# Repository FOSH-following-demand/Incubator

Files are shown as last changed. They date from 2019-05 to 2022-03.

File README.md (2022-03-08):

# Incubator

MboaLab in Cameroon were awarded a $750 grant by the Build Free and Open Science Hardware Project led by Andre Chagas and supported by the Mozilla Foundation to build a low-cost, open-source incubator for microbiology.

**Why an incubator?**
Most biology labs in Cameroon and elsewhere in resource-constrained contexts are under-equipped due to the high cost of lab equipment and it is essential for many protocols including open enzyme manufacturing to have optimal growth temperature for important microrganisms such as _Escherichia coli_ bacteria. 

**Why open hardware?**
We believe that DIY and Open Science Hardware can facilitate access to low-cost and high-quality equipment for biology labs in Cameroon, Ghana and beyond. 

All resources are openly licensed and linked below. Future plans include the inclusion of orbital shaking which increases aeration of cultures and therefore the yield of micro-organisms and their products like proteins.

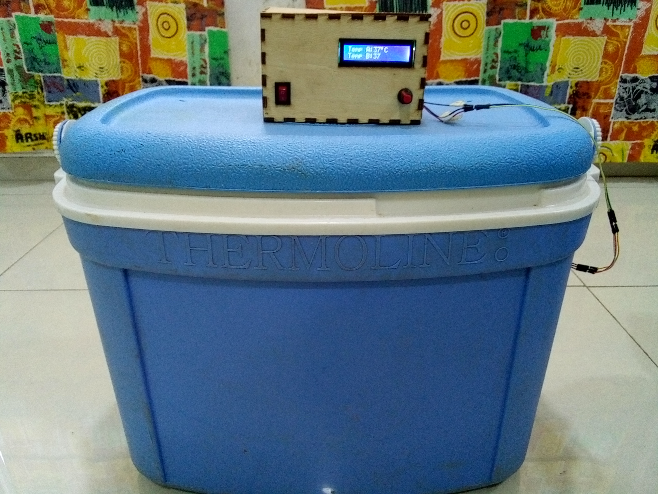
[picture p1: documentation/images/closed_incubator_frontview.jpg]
closed incubator frontview


# Build you own incubator

 - If you would like to build the device, get started by following the [build documentation](https://github.com/FOSH-following-demand/Incubator/tree/master/documentation/building)
 - The folders in this repository contain details of the [materials needed](https://github.com/FOSH-following-demand/Incubator/tree/master/hardware/BOM), laser cut design for the [enclosure](https://github.com/FOSH-following-demand/Incubator/tree/master/hardware/enclosure), the Arduino-based [electronics design](https://github.com/FOSH-following-demand/Incubator/tree/master/hardware/electronics) and firmware.
 - If you have questions or suggestions for improvements, please [add an issue](https://github.com/FOSH-following-demand/Incubator/issues) or make a pull request.

# Related Links

-   Documentation of Hive BioLab build on [Benchling](https://benchling.com/harry_akligoh/f/lib_UTO5lXRH-hive-biolab/etr_TNTAtGl7-building-and-testing-a-37-deg-celsius-incubator/edit)
-   Documentation of Hive BioLab build on [WikiFactory](https://wikifactory.com/+biolabkh/incubator)

# Acknowledgements

-   Ongola FabLab and OER Cameroon Team: Ariel Kameni and Yves Obame
-   Kumasi Hive Makerspace Team: Evans Tetteh-Djangbah and Isaac Atia-Abugbilla 
-   Image credits for Incubator: MboaLab Team

# Licensing

Software released under [MIT License](https://opensource.org/licenses/MIT) //
Hardware released under [CERN Open Hardware License v1.2](https://ohwr.org/cern_ohl_s_v2.txt)

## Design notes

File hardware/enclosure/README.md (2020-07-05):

### Summary

This folder contains 2D CAD files designed to be laser cut in 4 mm plywood or acrylic to form the electronics casing to be mounted on top of the cooler box.
Both PDF and dxf files are provided to suit different laser cutter requirements.

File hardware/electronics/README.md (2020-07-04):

## Electronics Diagram

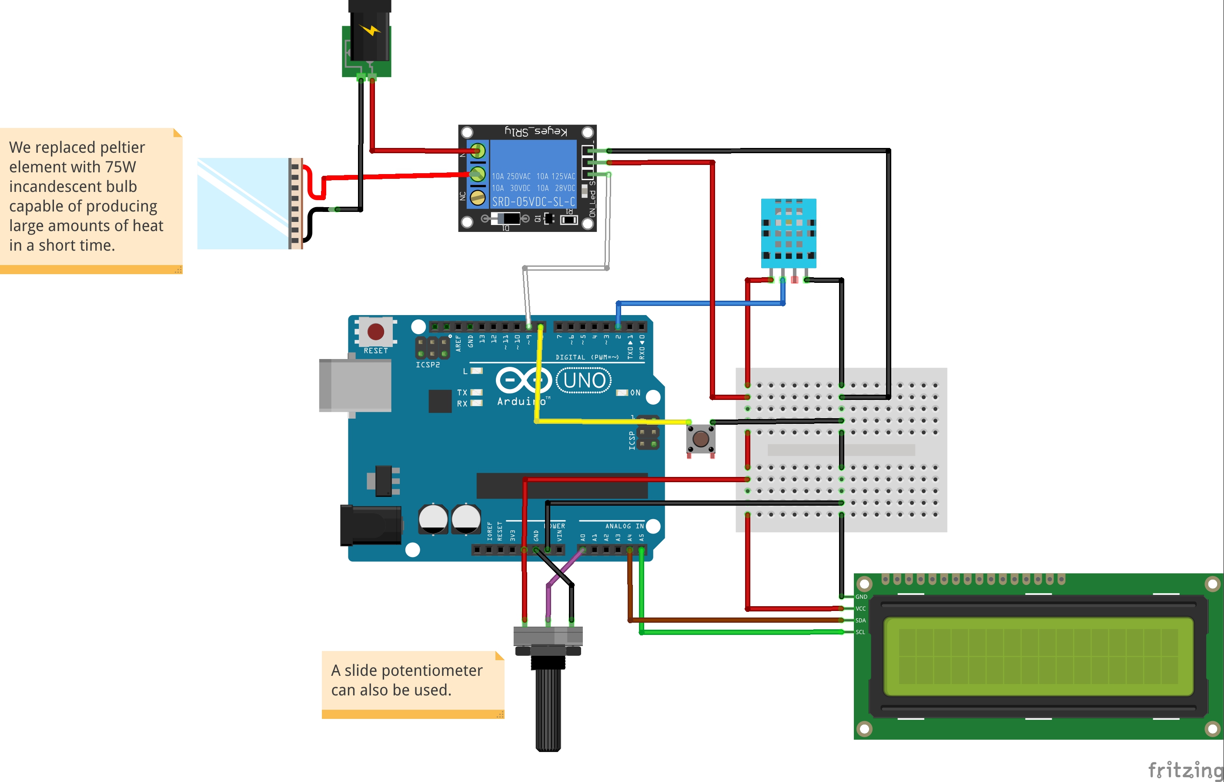
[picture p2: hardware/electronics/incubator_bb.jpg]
Arduino diagram


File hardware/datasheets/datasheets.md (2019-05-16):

#### Add to this folder all the datasheets used in the build.

This will make it easier for people to learn what each part is doing in case they need to substitute parts.

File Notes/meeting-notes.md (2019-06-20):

## June 20, 2019

Note taker: Julieta

- Incubator is working well, will test with yoghurt making tomorrow.
- Will complete info on local suppliers this week, with the link Andre provided
- Will upload arduino code and the laser cut patterns to the repo

The team wants to try making the shaker, as it's very easy and they have the materials, will take one or two days.

In terms of usability and democratization, next step is producing a "KossamTor" - An incubator for Kossam (yoghurt), that will be installed in the village for people to produce yoghurt. Presentation will be 3rd july, during MboaLab opendoors day. For this, the team will make a video and short instructions, for people that don't use GitHub (most of them).

Will try to buy stuff asap so to send Andre the invoices before 24th.

## June 14, 2019

Note taker: Julieta

1- Updates on development of the prototype     
- Assembled 1st version of incubator and it works!
- You can actually choose temperature :D

2- Document for the user
- BoM ready with $ (check hw folder BoM)
- Send information for contributing to map of suppliers --> Possible output of BFOSH: map with suppliers

3- Next
- Let's complete the docs: hw/datasheets, software: the code, readme file: steps to build it, steps to use it, any lesson learned, specifics people need to know to replicate the incubator??
- Test incubator by making yoghurt!

Next call: June 20th

## June 6, 2019

Note taker: Julieta

1- Updates on development of the prototype     
- Tested how long the chamber can keep hot water -- document this test! Maybe a journal can help, so documentation is not done at the end of the project (it's a pain and we tend to document only success)
- Started coding with Arduino IDE based on Biohack Academy's code combined with Richard Boman's incubator (biomakers challenge)
- Still working on the code, will upload 1st version soon

2- Program schedule, week 3: BoM, dev plan     
- Materials: goal is to get everything locally. Got sensors in mboa lab, but trying to source them locally (in progress). 
- Get BoM & simple dev plan, will 

3- Difficulties      
- Still learning github - Julieta will record & send video tutorial 

Next call: June 13th

## May 30, 2019

Notetaker: Andre

Status:
 - Made document showing different materials other projects used.
 - Decided for the cooler box, since this is already built and has been optimized for holding temperature.
 - They also saw a shop that repairs fridges, maybe using an out of order fridge, might be an option (to be tested later maybe)
 - Found temperature sensor kits and Arduino at Mboalab. 

Questions:

 - how to test the incubator to know that it is working? and how can people building it will know that their built is working? (testing and calibration).
 - Would it be possible to log the data? Register the temperature being read by the arduino in a file, so that the data can be plotted later.

before next meeting:
 
 - Write down a BOM and Document! https://github.com/FOSH-following-demand/Incubator/blob/master/hardware/BOM/BOM.md

Next meeting:

- Agenda:  
 
 -- check how the building of the first prototype is going, see if there are any problems.   
 -- If things are already working properly, think about testing/calibrating and writing a manual for other people to build.  
 
## May 23, 2019

Status quo on the project:

Questions: What material to use for the frame - wood, metal, which metal - should be low-cost and durable.
Options: impregnated wood or insulated with styrophome

Local suppliers in Yaoundé - add to this list: https://github.com/FOSH-following-demand/local_suppliers/blob/master/electronic_components.csv

Next local meeting Friday, May 24
- Agenda items:

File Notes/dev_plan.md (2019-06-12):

# Development plan

Use this file to store your plan for the program. What are you going to do, in which order? 

| Week        | Activities           | Who           |
| ----------- | -------------------- | ------------- |
| 1           |Research existing work related to incubator                |  Thomas and Yves             |
| 2           |What material to use for the frame                      |Lenshina and Yves              |
| 3           |Find Local suppliers and buy equipment                       |Lenshina, Thomas, Ariel, Marius|
| 4           |Build the electronic Part                     | Lenshina, Thomas, Yves, Marius, Ariel              |
| 5           |Assemble the Version 1 of the Incubator. Start the Shaker                      |Lenshina, Thomas, Yves, Marius, Ariel |

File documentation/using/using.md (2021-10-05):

## DIY Incubator Operation Manual

### Installation and Setup 

The DIY incubator is top-opened. The latter should be placed on a low-level surface to facilitate handling and use.

1. Make sure that the incubator is off and plug-in the power cable on normal sector current (220V-240V);
 
2. Switch on the device using the power button located at the level of the control box. (The incandescent bulb within the incubator should light up and information about the temperature inside the cooler box should be displayed on the LCD screen);

3. Place desired items inside the cooler box; (While placing items in the cooler box, care must be taken to avoid direct contact with the incandescent bulb).
 
4. Close the lid of the cooler box;
 
5. Use the potentiometer (rotary button) of the electronic control box to input the desired temperature. 
*(The light bulb will stay on until the desired temperature is obtained inside the cooler box; Once the desired temperature is obtained, the incandescent bulb will then start to continuously come on and off to regulate and maintain the temperature stable inside the cooler box).*
 
6. To stop the incubator, switch off the power button. 
*(No program option to time the incubation is currently available, Use an external timer during operation).*

### Handling routine:
The DIY incubator should be thoroughly disinfected and cleaned before and after each incubation.

### Features:
The device has an auto-resume function (in case of power outage, the incubation will automatically continue as soon as current is back with set conditions maintained without any external internvention needed);

### Troubleshooting:
a.  The LCD screen is on but the incandescent bulb doesn’t turn on:
1.  replace the bulb;
2.  replace the bulb holder;
3.  replace the I2C relay module

Links:
https://openbioeconomy.org/projects/open-source-microbiology-incubator/
https://github.com/FOSH-following-demand/Incubator/tree/master/software

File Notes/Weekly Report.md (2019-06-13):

Brief summary of the progress made, learnings, and way forward in keywords by week

#### Week1
We have made a list of similar DIY incubator projects. In addition to this, Andre sent us several links to other incubator projects.  

#### Week 2
We did a reseach on What material to use for the frame (wood, metal, which metal - should be low-cost and durable). Finally we come out with this comparative table and we decide to use the cooler box. 

| Type of Material used for Incubator Shell/Insulation material | Pros                                                                                                                      | Cons                                                                                                                                                          | Optimisation                     |
|---------------------------------------------------------------|---------------------------------------------------------------------------------------------------------------------------|---------------------------------------------------------------------------------------------------------------------------------------------------------------|----------------------------------|
| Acrylic                                                       | ·      Attractive visibly                                                                                                 | Expensive                                                                                                                                                     | N/A                              |
|                                                               | ·      Does not require any manual work/designing as all parts are sculpted and cut using the 3D printer and laser cutter |                                                                                                                                                               |                                  |
|                                                               |                                                                                                                           | 3D printer and laser cutter required to assemble parts                                                                                                        |                                  |
| Wood/plywood                                                  | ·      Cheap and available locally                                                                                        | Liable to rot due microorganisms and moisture                                                                                                                 | Impregnating                     |
|                                                               | ·      Light and can easily be incorporated in field models                                                               | Plywood breaks if not carefully handled                                                                                                                       |                                  |
|                                                               |                                                                                                                           |                                                                                                                                                               |                                  |
| Glass                                                         | ·      Attractive visibly                                                                                                 | Fragile to work with as  it breaks easily                                                                                                                     | N/A                              |
|                                                               |                                                                                                                           |                                                                                                                                                               |                                  |
| Stainless Steel sheet metal                                   | ·      Rust and corrosion- resistant                                                                                      | ·      Expensive                                                                                                                                              | N/A                              |
|                                                               | ·      Easy to clean                                                                                                      | ·      Prone to overheating                                                                                                                                   |                                  |
|                                                               |                                                                                                                           | ·      Heavy                                                                                                                                                  |                                  |
|                                                               |                                                                                                                           |                                                                                                                                                               |                                  |
| Polystyrene foam (Styrofoam) box                              | ·      Cheap and available locally                                                                                        | Favours bacterial and fungal growth                                                                                                                           | N/A                              |
|                                                               | ·      Light and can easily be incorporated in field models                                                               | Can be damaged in the process of cleaning/sterilisation                                                                                                       |                                  |
|                                                               | ·      Recommended to achieve lower ambient temperatures (< 25 °C),                                                       | Melts easily in case of over heating                                                                                                                          |                                  |
| Hard Plastic cooler box                                       | ·      Cheap and available locally                                                                                        |                                                                                                                                                               | N/A                              |
|                                                               | ·      Easy to clean and sterilize                                                                                        |                                                                                                                                                               |                                  |
|                                                               | ·      Can achieve a set temperature of 37 °C to 44.5 °C                                                                  |                                                                                                                                                               |                                  |
|                                                               | ·      Takes less time approximately 45 - 96 minutes to reach set temperature                                             |                                                                                                                                                               |                                  |
|                                                               | ·      Energy consumption stands at 0.78 - 1.05 kWh/24h in cold environments (3.5 to 7.5 °C)                              |                                                                                                                                                               |                                  |
| Cardboard box                                                 | ·      Cheap and readily available                                                                                        | ·      Not waterproof so easily gets destroyed by moisture                                                                                                    | Insulating with polystyrene foam |
|                                                               | ·      Light and can easily be incorporated in field models                                                               | ·      Not heat-resistant so gets burned in case of over heating                                                                                              |                                  |
|                                                               |                                                                                                                           | ·      Incubator shell has to be shut tight to avoid heat dissipation and this is very difficult to achieve with cardboard boxes without the survival blanket |                                  |
|                                                               |                                                                                                                           | ·      Not recommended for use at lower ambient temperatures since this set up with similar to slightly                                                       |                                  |
|                                                               |                                                                                                                           | ·      Greater power consumption observed                                                                                                                     |                                  |

#### Week 3
The team was so glad to found local suppliers selling all what we need here in Cameroon: DBL electronics and Megatec

| Name of the local suppliers  | Localisation on google map                | Contact                                                                                                                   |
|------------------------------|-------------------------------------------|---------------------------------------------------------------------------------------------------------------------------|
| DBL electronique             | https://maps.app.goo.gl/5ZiqXomu7RbgKoKo7 |  - Yaoundé (+237698282538/+237673687133) - Douala (+237699675349/+237678830266) - Bafoussam (+237668095091/+237605076456) |
| Megatec Electronic           | https://maps.app.goo.gl/c4DdAgbu1jX4qPhZ9 | +237677524208                                                                                                             |

#### Week4
This week was so productive, we focus our efforts on electronics: 
- First of all, we decided on what we want our incubator will be able to do. Specifically, we want to be able to fixe the desired temperature with a potentiometer and bring the incubator at this temperature.  
- We had an issue on the cooling system of the incubator. Fan VS Peltier elements. Finally we choose the Peltier element
- We bought the required electronics
- Ariel from Ongola Fablab, helps us with the Arduino code and all looks great

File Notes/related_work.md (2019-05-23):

# Related projects

| Project name  | URL           | Active/Not active | Notes - relevance |
| ------------- | ------------- | ----------------- | -------------- |
| Hackteria| https://hackteria.org/wiki/index.php/DIY_Incubator| Active | |
| Biodesign| https://biodesign.cc/2013/12/25/diy-incubator/ | Active |  |
| Instructables|https://www.instructables.com/id/Low-cost-and-accurate-incubator-for-DIY-biology/|Active|  |
|Biomaker|https://www.biomaker.org/projects/2018/1/29/open-source-lasercut-portable-incubator-for-microbiology|Active|

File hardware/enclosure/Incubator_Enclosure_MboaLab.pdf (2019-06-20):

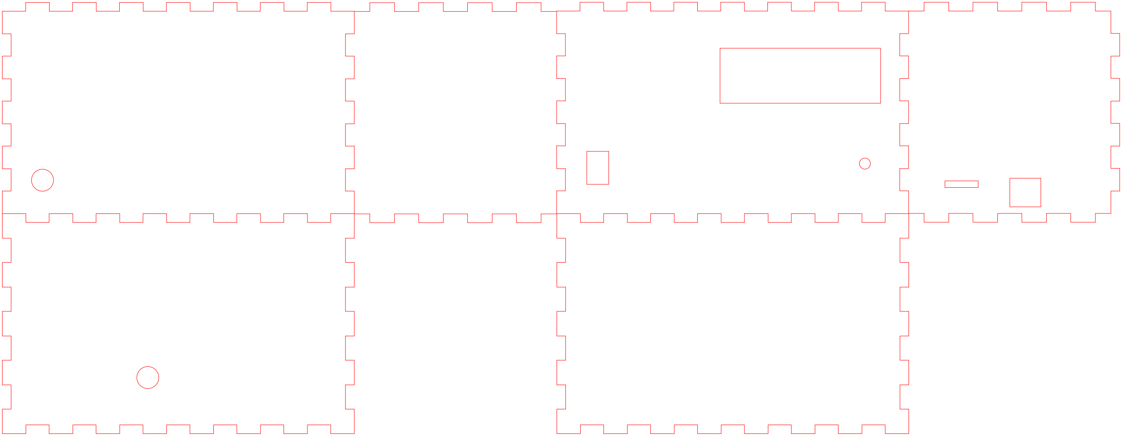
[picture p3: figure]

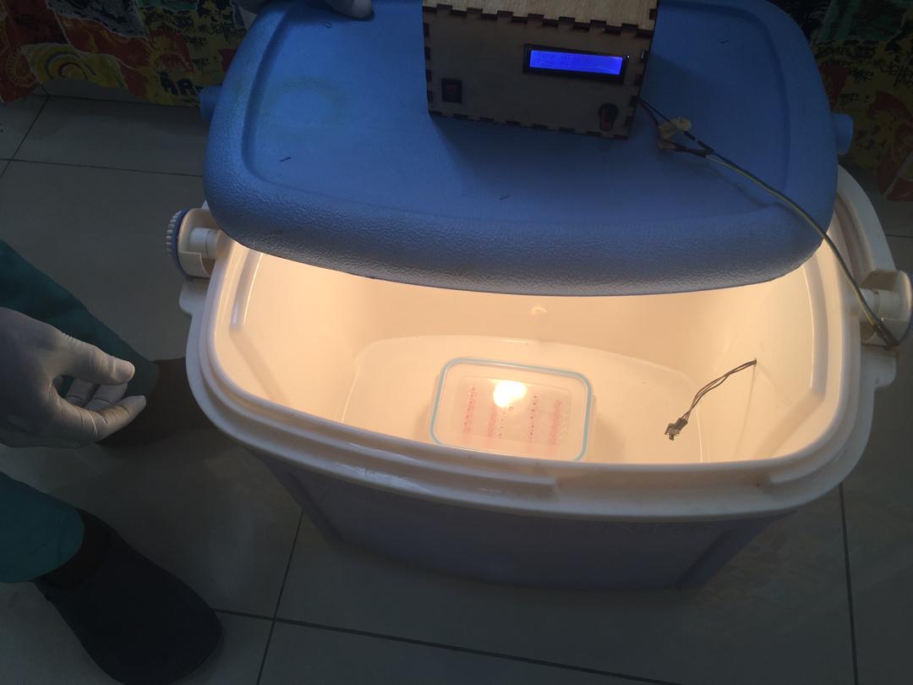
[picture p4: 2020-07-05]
documentation/images/open_incubator_topview.jpg

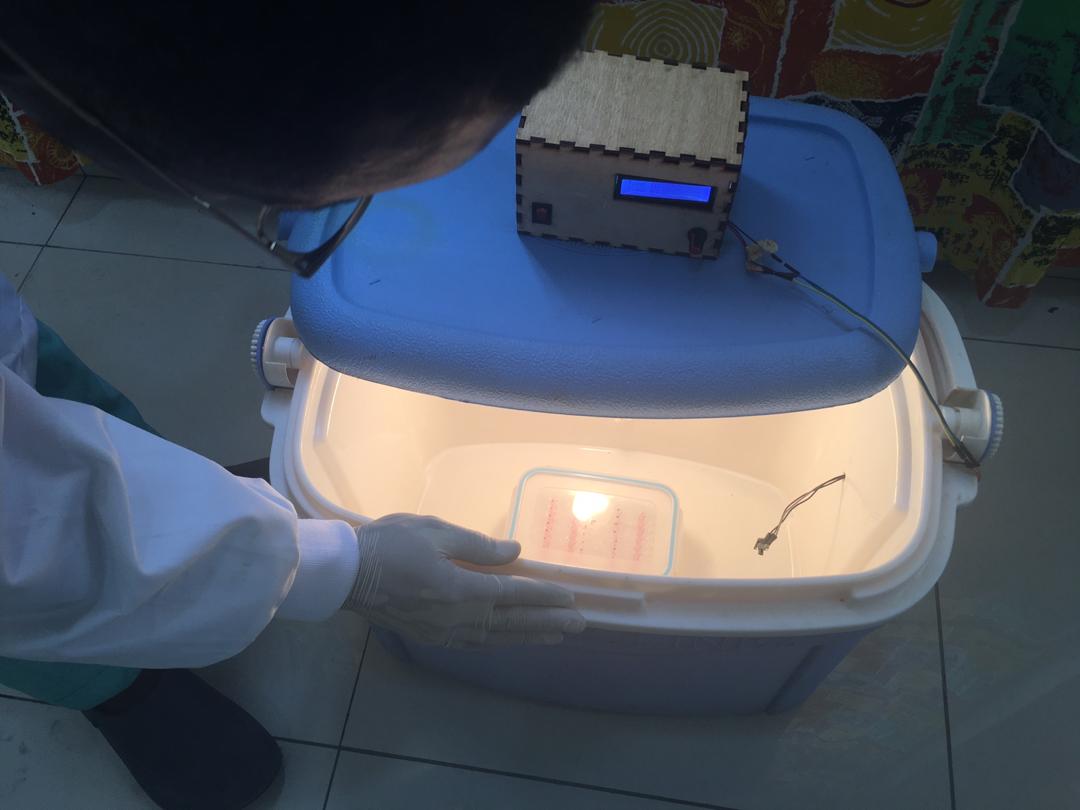
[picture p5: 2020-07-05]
documentation/images/open_incubator_topview2.jpg

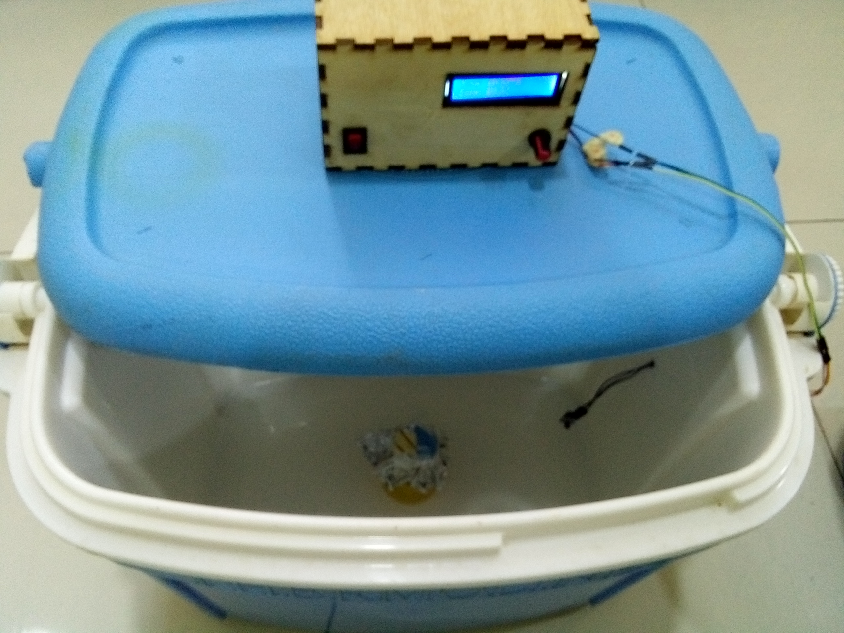
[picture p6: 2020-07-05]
documentation/images/closed_incubator_topview.jpg

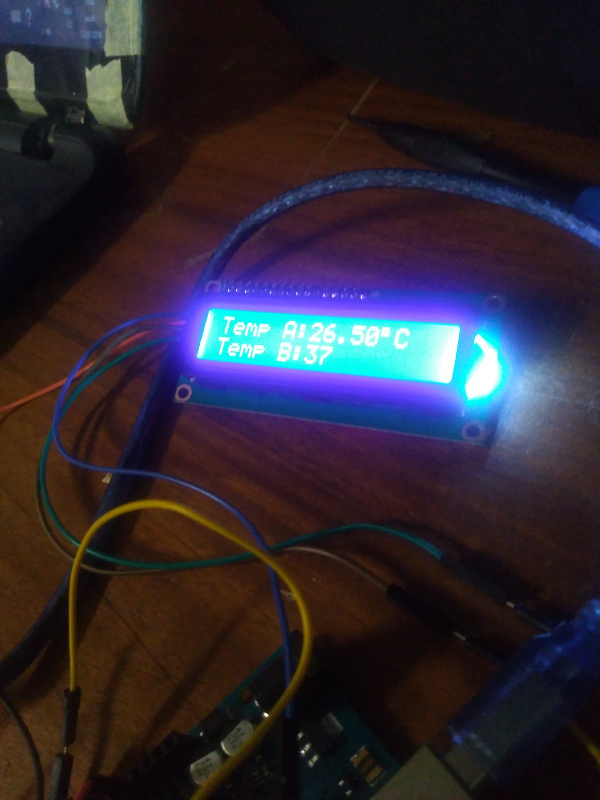
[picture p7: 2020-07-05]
documentation/images/lcd_display.jpg

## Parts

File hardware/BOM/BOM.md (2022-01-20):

## Electronics and Hardware
| N° | Quantity | Description                 | Local supplier   | Cost (F CFA) | Datasheet |
|----|--------|-----------------            |------------------|--------------|--------------|
| 1  | 1      | Arduino Uno (Version: Rev.3)                | [DBL Electronique]| 7000         | [Datasheet](https://github.com/FOSH-following-demand/Incubator/blob/master/hardware/datasheets/Arduino_Uno.pdf) |
| 2  | 1      | 1602 LCD Display Module (1602A-1)     | DBL Electronique | 3000         | [Datasheet](https://github.com/FOSH-following-demand/Incubator/blob/master/hardware/datasheets/1602A.pdf)|
| 3  | 1      | 1-Channel 5V  I2C Relay Module for Arduino | DBL Electronique | 1500         | [Datasheet](https://github.com/FOSH-following-demand/Incubator/blob/master/hardware/datasheets/Datasheet%20for%20ELC3003.pdf)          |
| 4  | 1      | Step Down Power Supply Module (Hi-Link HLK-PM01 AC-DC 100-240V to 5V DC/3W  | DBL Electronique | 3000         | [Datasheet](https://github.com/FOSH-following-demand/Incubator/blob/master/hardware/datasheets/HLK-PM01-Hi-Link_Step%20Down%20Power%20Supply%20Module.pdf)          |
| 5  | 1      | Temperature Sensor 18B20                  | DBL Electronique | 3500         | [Datasheet](https://github.com/FOSH-following-demand/Incubator/blob/master/hardware/datasheets/DS18B20.pdf)|
| 6  | 1      | USB 2.0 A to B Cable (Model Number:U022-010-R)             | DBL Electronique | 1000         | [Datasheet](https://github.com/FOSH-following-demand/Incubator/blob/master/hardware/datasheets/1951363_USB%20Cable.pdf)          |
| 7  | 10     | Jumper Wires (Male to Male) 40 x 6" (150mm) Adafruit PRODUCT ID: 758 | DBL Electronique | 2000          |  [Datasheet](https://github.com/FOSH-following-demand/Incubator/blob/master/hardware/datasheets/758_Web_Jumper%20wire.pdf)         |
| 8  | 10     | Dupont Wire (20CM, Color Jumper Cable, 2.54mm 1P-1P Male to Female)                | DBL Electronique | 2000          | [Datasheet](https://github.com/FOSH-following-demand/Incubator/blob/master/hardware/datasheets/40P-MF-Dupont-Wire.pdf)          |
| 9  | 1      | Rotary Potentiometer - 100k Ohm, Linear, Panel Mount*               | DBL Electronique | 250          | [Datasheet](https://github.com/FOSH-following-demand/Incubator/blob/master/hardware/datasheets/Rotary%20PDB18.pdf)          |
| 10 | 1      | Breadboard Solderless ABS, 7mm to 8mm (Part Number MCBB400)              | DBL Electronique | 1500         | [Datasheet](https://github.com/FOSH-following-demand/Incubator/blob/master/hardware/datasheets/Breadboard-roboromania.pdf)          |
| 11 | 1      | Standard IEC 1.5mm Electrical cable, PVC Flexible Cable 3 Core White in 1M Cut Length | DBL Electronique | 2500         | [Product Info](https://www.electricpoint.com/3093y-1-5mm-pvc-flexible-cable-three-core-white-1m.html)          |
| 12 | 1      | Incandescent bulb A60 Frosted Glass 75W 240V*          | Hardware store   |500           | [Product Info](https://shengfeng.en.made-in-china.com/product/myWnqOVUEehM/China-A60-Incandescent-Bulbs-Light-Frosted-Glass-75W-240V-Ce-RoHS.html)         |
| 13 | 1      | Light Bulb Holder, 10x E27 ES Edison Screw Cap Socket Light Bulb Holder Fitting Lamp Fixing Base          | Hardware store  |2000           | [Product Info](https://www.amazon.co.uk/Edison-Socket-Holder-Fitting-Fixing/dp/B01NBSVVJ2)           |
| 14 | 1      | Cooler box Thermoline® 50x30 cm*               | Local Markets    | 25 000       |     /      |
| 15 | 1      | 4 mm plywood or colored acrylic                 | Local Markets    |    /    |     /      |
| 16 | 1      | ON/Off Red LED Light illuminated Rocker Switch (RL-15-11/N-C-2-RE/BK-P1-S-2)  | DBL Electronique| 600  | [Datasheet](https://github.com/FOSH-following-demand/Incubator/blob/master/hardware/datasheets/Rocker-switches.pdf)           |
| 17 | 1      | Wood glue, Top bond® white adhesive wood glue,500g    | Hardware store| 2000  | [Product Info](https://m.made-in-china.com/product/Good-Price-Top-Bond-Furniture-White-Adhesive-Liquid-Wood-Glue-832258715.html)  |
| 17 | 1      | Acrylic glue, WELD-ON 4 Acrylic Adhesive - 4 Oz + Applicator Bottle with Needle | Hardware store| 10000  | [Product Info](https://www.amazon.com/Weld-Acrylic-Adhesive-Applicator-Bottle/dp/B0096TWKCW/?&tag=gluefaq-20#descriptionAndDetails)  |
| 18 | 1      | GOLDSCREW PZ DOUBLE-COUNTERSUNK MULTIPURPOSE SCREWS 5 X 50MM 200 PACK (16497) | Hardware store| 4000  | [Product Info](https://www.screwfix.com/p/goldscrew-pz-double-countersunk-multipurpose-screws-5-x-50mm-200-pack/16497#product_additional_details_container)  |

* The lightbulb could be replaced with another heater e.g. a PCB heater element or a Peltier element
* Rotary potentiometer could also be used
* Other cooler box dimension could be used (100W Incandescent bulb should be usef for bigger cooler boxes)

## Mechanical

- Laser Cutter 
- Electric drill

## Tools

- Soldering kit
- Universal Screwdriver
- Double-sided tape
- Digital multimeter
- Wire cutter

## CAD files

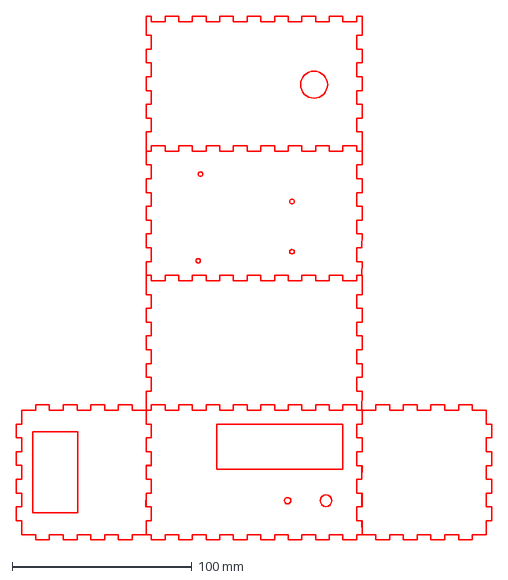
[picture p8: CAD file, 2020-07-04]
hardware/enclosure/Incubator_Enclosure_Hive.dxf
264.0 x 291.0 mm

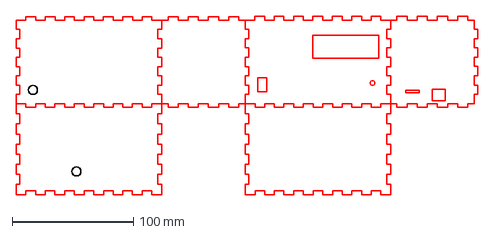
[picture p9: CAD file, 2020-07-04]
hardware/enclosure/Incubator_Enclosure_MboaLab.dxf
381.0 x 147.1 mm

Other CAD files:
hardware/enclosure/Incubator_Enclosure_Hive.dwg

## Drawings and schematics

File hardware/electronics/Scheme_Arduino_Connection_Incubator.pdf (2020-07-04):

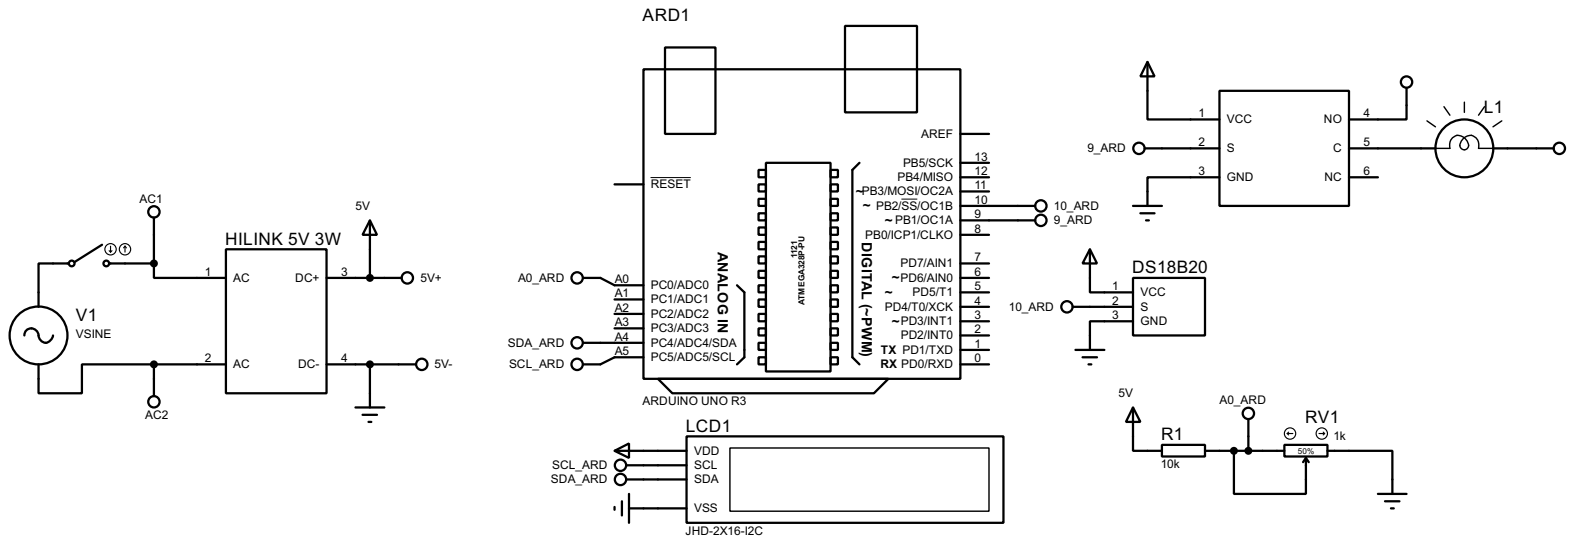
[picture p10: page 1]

DIGITAL (~PWM) ANALOG IN ATMEGA328P-PU 1121 ~~ ~~~~ TXRX PD0/RXD 0 PD1/TXD 1 PD2/INT0 2 PD3/INT1 3 PD4/T0/XCK 4 PD5/T1 5 PD6/AIN0 6 PD7/AIN1 7 PB0/ICP1/CLKO 8 PB1/OC1A 9 PB2/SS/OC1B 10 PB3/MOSI/OC2A 11 PB4/MISO 12 PB5/SCK 13 AREF PC5/ADC5/SCL A5 PC4/ADC4/SDA A4 PC3/ADC3 A3 PC2/ADC2 A2 PC1/ADC1 A1 PC0/ADC0 A0 RESET ARD1 ARDUINO UNO R3 R1 10k 50%RV11k VSS SCL VDD SDA LCD1 JHD-2X16-I2C L1 5V AC 1 AC 2 DC+ 3 DC- 4 HILINK 5V 3W V1 VSINE 5V AC1 AC2 5V+5V- SCL_ARD SDA_ARD SDA_ARD SCL_ARD VCC 1 S 2 GND 3 NO 4 C 5 NC 6 9_ARD 9_ARD 10_ARD A0_ARD VCC 1 S 2 GND 3 DS18B20 10_ARD A0_ARD

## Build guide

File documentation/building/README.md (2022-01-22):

## Getting started with assembly

This equipment is an incubator, designed to keep the contents at a constant temperature above the ambient temperature. It is an insulated box (a cooler box) that contains a heater (lightbulb), a temperature sensor and some electronics and software that will control the temperature to keep it constant at the level input by the user.

The primary use case is microbiology. It is essential for many protocols to have optimal growth temperature for important microrganisms such as _Escherichia coli_ bacteria. However, mst biology labs in Cameroon and elsewhere in resource-constrained contexts are under-equipped due to the high cost of lab equipment. Other use cases include a drying chamber and a yoghurt maker.

To build the device you will need to undertake some basic soldering and load software onto an Arduino Uno microcontroller but you do not need to have prior experience as there are many tutorials and guides online. This build could be completed by one person in less than a day with all materials and facilities available.

If you have questions you can contact [@LabMboa](https://twitter.com/labmboa?lang=en) on Twitter or via email mboalab@gmail.com

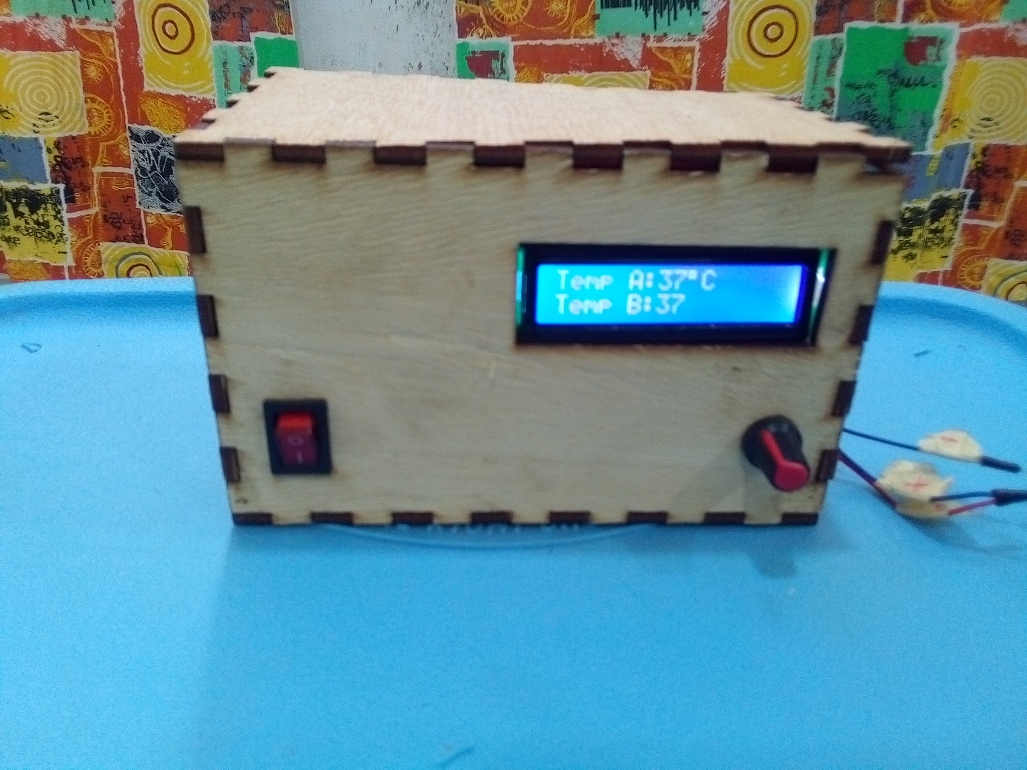
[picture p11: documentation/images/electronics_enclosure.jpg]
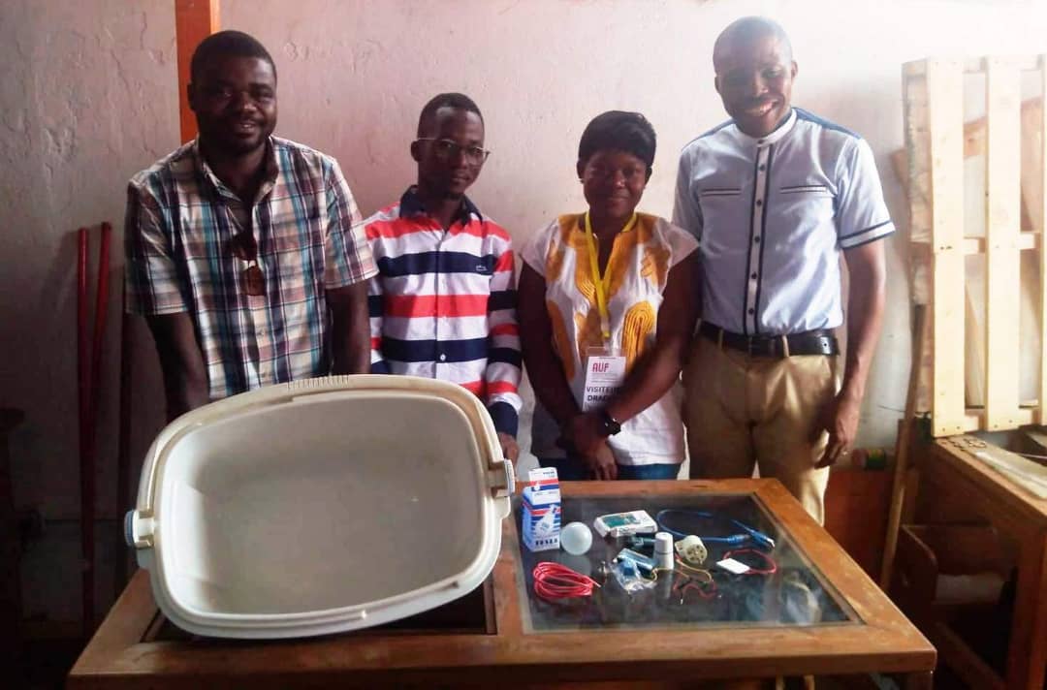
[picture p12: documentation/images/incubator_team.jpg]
   
<br>

## Gathering your materials

The list of components and tools required can be found in the [Bill of Materials](https://github.com/FOSH-following-demand/Incubator/blob/master/hardware/BOM/BOM.md). 

<br>

## Build Steps

### Assembling the electronics
1.	Gather all necessary equipment, electronics and sensors listed in the [BOM](https://github.com/FOSH-following-demand/Incubator/blob/88bb84b1b9b74473d8da1b99ba0d825d767e2a87/hardware/BOM/BOM.md), keep your soldering kit and Digital multimeter ready to check connections and normal operation after soldering. 
2.	Using jumpers and dupont wires, Carefully connect all the sensors and other modules to the Arduino Uno Rev.3 microprocessor and to the breadboard following the equipment’s [electronic circuit diagrams](https://github.com/FOSH-following-demand/Incubator/blob/88bb84b1b9b74473d8da1b99ba0d825d767e2a87/hardware/electronics/incubator_bb.jpg). Use a standard IEC 1.5mm Electrical cable to connect the relay module, light bulb and power supply module.
3.	Using a digital multimeter, check all connections and the normal flows of current in the whole electric circuit.

### Uploading the software to the arduino board
4.	Connect the Arduino UNO board to a computer with the latest version of [Arduino IDE](https://www.arduino.cc/en/software) installed using a USB 2.0 A to B Cable.
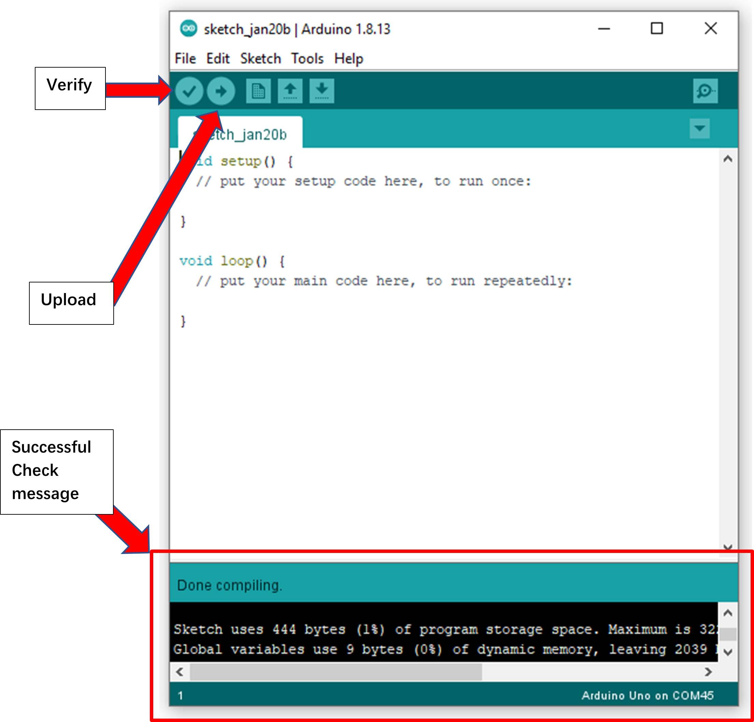
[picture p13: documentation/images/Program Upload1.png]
5.	Open the [Incubator.ino](https://github.com/FOSH-following-demand/Incubator/blob/88bb84b1b9b74473d8da1b99ba0d825d767e2a87/software/Incubator.ino) software and on the software interface, click on **verify** to make sure all necessary libraries are installed. Wait until the message **Done compiling** and specific information about the program appears as shown on the picture  .   
6.	Select the right port and on the software interface click on **upload** to upload the program to the board. Wait until the message **Done uploading** is displayed. 

### Constructing the electronics enclosure and Integrating the electronics
7.	Use the 2D CAD file: [Incubator_Enclosure](https://github.com/FOSH-following-demand/Incubator/blob/88bb84b1b9b74473d8da1b99ba0d825d767e2a87/hardware/enclosure/Incubator_Enclosure_MboaLab.pdf), to laser-cut plywood or acrylic to make the electronic enclosure of the incubator. 5mm colored acrylic or 4mm plywood is recommended. Use acrylic glue or Wood glue to assemble cut pieces and first mount the base of the box. 
8.	At this point, place the base above the cooler box cover at the location you want the electronic box to fit (center position preferred); 
9.	Use an electric drill to make a hole (1cm) crossing the acrylic and the entire depth of the cooler box cover.
10.	Drill another hole (1cm) on the side, just below the handle of the cooler box.
11.	Send the temperature sensor inside the cooler box through the created hole on the side. 
12.	Send light bulb cable through the created hole on the cooler box cover and carefully place all electronic parts inside the electronics enclosure.
13.	Use double side tape to fix the electronic enclosure to the cooler box cover.
14.	Screw the bulb holder on the donwnside of the cooler box cover and place an incandescent bulb. 
15.	Turn on the circuit and check if the light bulb is switched on and other sensors are operational.
16.	Place the cover of the electronic box (don’t use acrylic glue or Wood glue to seal the box) the cover should remain easily removable for maintenance.

### Checking that it works
17.	Use a separate thermometer to verify that the temperature reaches and is maintained at the correct set point.
18.	Check and follow [Using](https://github.com/FOSH-following-demand/Incubator/blob/e79139635490b86b92911df16381e2448330a7f6/documentation/using/using.md) for Operation Manual to ensure normal use and behavior of the equipment.

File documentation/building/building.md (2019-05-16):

**Use this folder to create files for building instructions:**
- Each equipment is going to have a different building process, but here are some suggestions on how to organise things:

<br>

1. getting started:
 - a brief overview of the equipment people are about to build and what kind of knowledge they are expected to have (soldering, programming). Also, is this safe for amateurs/kids? Is it a one person build? How much time does it take on average to build it?
 - Could you add contact information (email, forum, twitter handle) for people to reach out in case something goes wrong?

<br>

2. List of materials needed:
 - In the form of a table, containing part name, quantity and a couple of words on what they do. Extra points if the parts are divided according to the building steps (below)
 - Remember to include the tools necessary as well! (pliers, saw, computer, etc)  

 |part name| function  | quantity  | build step  | obs.  |
 |---|---|---|---|---|
 |LM2596| voltage regulator  | 2  | 3  | these could be substituted by XX  |
 | Nose needle Pliers  | hold components while soldering  | 1  | all steps  | regular pliers would also work  |

<br>

3. build steps:
 - Divide this section in as many subparts as you like and try to be as clear as possible. Would someone seeing the whole thing for the first time be able to build it? (it is a good exercise to oversee someone building the equipment using only your written/video/figure instructions)
 - Is a video a better way to instruct people how to use it? try to keep the file size as small as possible without compromising quality. Also reach out to us, as a good idea might be to create a different repository for the video files.  

<br>

4. Last checks before powering up/using for the first time:
 - Could people do one more check of everything before powering up things? Maybe double check that the capacitors were soldered in the proper orientation? Make sure there are no cut metal parts shorting the bottom side of the PCB? Make sure the area around the equipment is clear and won't be hit if the equipment has moving parts (eg shakers, centrifuges, etc).

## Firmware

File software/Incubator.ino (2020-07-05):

#include <Wire.h> 
#include <LiquidCrystal_I2C.h>
// #include <OneWire.h>
// #include <DallasTemperature.h>
// #define ONE_WIRE_BUS 2

// OneWire oneWire(ONE_WIRE_BUS);
// DallasTemperature sensors(&oneWire);
#include "DHT.h"

#define DHTPIN 2 
#define DHTTYPE DHT11
DHT dht(DHTPIN, DHTTYPE);
LiquidCrystal_I2C lcd(0x38, 16, 2);

int startButton = 8;
int buttonState;
int heatPin = 9;
double temp_value = 0;
int pot = A0;
int pot_value;
double curTemp;
double prevTemp;
double max_temp = 0;


double set_pot() {
  pot_value = analogRead(pot);
  double max_value = map(pot_value, 0, 1023, 0, 100); //This is the desired temperature value
  return max_value;
}

long convert_time(long millisec) {
  int seconds = millisec/1000;
  if (seconds < 60) {
    lcd.print(seconds);
    lcd.print("secs");
  } else if (seconds == 60) {
    int minutes = seconds/60;
    lcd.print(minutes);
    lcd.print("mins");
  }
}


boolean heatUp(double desired_temp) {
  unsigned long startTime = millis();
  // sensors.requestTemperatures();
  curTemp = dht.readTemperature();
  // Serial.print(curTemp);
  lcd.setCursor(0,1);
  lcd.print("Temp: ");
  lcd.print(curTemp);
  lcd.print((char)223);
  lcd.print("C");
  while (curTemp < desired_temp) {
    int pulseDuration = min(10000,20000);
    digitalWrite(heatPin,LOW);
    delay(pulseDuration);
    digitalWrite(heatPin,HIGH);

    // check if temperatue is equal to or more than desired temperature
    curTemp = dht.readTemperature();
    // Serial.print(curTemp);
    lcd.setCursor(0,1);
    lcd.print("Temp: ");
    lcd.print(curTemp);
    lcd.print((char)223);
    lcd.print("C");
    if (curTemp >= desired_temp)
    break;

    // Wait a little as we approach desired temperature to avoid overheating
    if ((desired_temp - curTemp) < 2){
      do {
        prevTemp = curTemp;
        delay(1000);
        curTemp = dht.readTemperature();
        lcd.setCursor(0,1);
        lcd.print("Temp: ");
        lcd.print(curTemp);
        lcd.print((char)223);
        lcd.print("C");
        // Serial.print(curTemp);
      } while(curTemp > prevTemp);
    }

    // check if temperature is equal to or more than desired temperature
    if (curTemp >= desired_temp)
    break;
  }
  return true;
}

void holdConstantTemp(double idealTemp) {
  while (true) {
    lcd.setCursor(0,1);
    lcd.print(idealTemp);
    lcd.print((char)223);
    lcd.print("C");
    curTemp = dht.readTemperature();
    Serial.print(curTemp);
    if (curTemp < idealTemp) {
      digitalWrite(heatPin,HIGH);
      delay(5000);
      digitalWrite(heatPin,LOW);
    } else if (curTemp > (idealTemp+0.5)) {
      digitalWrite(heatPin,HIGH); //Turning off source of heat so it cools down naturally
    }
    delay(2000);
  }
}

void runIncubator() {
  lcd.clear();
  delay(1000);
  lcd.setCursor(0,0);
  lcd.print("Set Temp:");
  while (true) {
    lcd.setCursor(9,0);
    temp_value = set_pot();
    lcd.print(temp_value);
    lcd.print((char)223);
    lcd.print("C");
    // Serial.println(temp_value);
    // Serial.println("deg Celcius");
    buttonState = digitalRead(startButton);
    if (buttonState == LOW) {
      break;
    }
    delay(1000);
   }
  unsigned long startTime = millis();
  delay(1000);
  lcd.clear();
  lcd.setCursor(0,0);
  lcd.print("HEATING UP");
  if (!heatUp(temp_value)) {
    lcd.clear();
    lcd.setCursor(0,0);
    lcd.print("Heat can't raise");
    lcd.setCursor(0,1);
    lcd.print("Something wrong");
  } else {
    //do nothing;
  }
  long timeElapsed = millis() - startTime;
  lcd.clear();
  lcd.setCursor(0,0);
  lcd.print("Total heat time");
  lcd.setCursor(0,1);
  lcd.print(convert_time(timeElapsed));
  // Serial.println();
  delay(2000);
  lcd.clear();
  lcd.setCursor(0,0);
  lcd.print("Holding temp");
    
  max_temp = temp_value;
  holdConstantTemp(max_temp);
}


void setup() {
  Serial.begin(9600);
  dht.begin();
  lcd.begin();
  lcd.backlight();
  pinMode(startButton,INPUT);
  pinMode(heatPin,OUTPUT);
  digitalWrite(startButton,HIGH);
  digitalWrite(heatPin,HIGH);
  lcd.setCursor(0,0);
  lcd.print("Starting in ");
  delay(1000);
  for (int i = 5; i > 0; i--) {
    lcd.setCursor(13,0);
    lcd.print(i);
    lcd.print("..");
    delay(1000);
  }
  runIncubator();
}

void loop() {
  // put your main code here, to run repeatedly:

}

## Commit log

2019-06-06 adding datasheet
    sensor datasheet (test)
2019-08-23 Updated Incubator.ino
    Faced numerous errors while using previouse Incubator arduino code. This is our fix.
2020-07-04 Changes folder name frame to enclosure
    [Laser_cut_part_dxf.dxf]
2020-07-04 Update and rename frame.md to README.md
2020-07-04 Added link to enclosure design folder
2020-07-04 Added sections to complete for assembly
2020-07-04 Added image and fritzing diagram
    [incubator.fzz]
2020-07-04 Added Hive laser files
    [Incubator_Enclosure_Hive.dwg, Incubator_Enclosure_Hive.dxf, Incubator_Enclosure_MboaLab.dxf]
2020-07-05 Added 4 mm plywood width
